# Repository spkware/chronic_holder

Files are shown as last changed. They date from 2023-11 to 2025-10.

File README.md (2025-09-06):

# ***indie*** - ***in***dependent ***d***ovetail ***i***mplants for ***e***lectrophysiology

**Please check out our [preprint](https://www.biorxiv.org/content/10.1101/2023.12.22.572441v2) for more details on the approach!** 

Design files and instructions for manufacturing NP1.0, NP2.0alpha, and NP2.0 Neuropixels chronic recording enclosures. 

**Please reach out to us if you want to try this approach, we need your input.** We are actively working on the instructions.

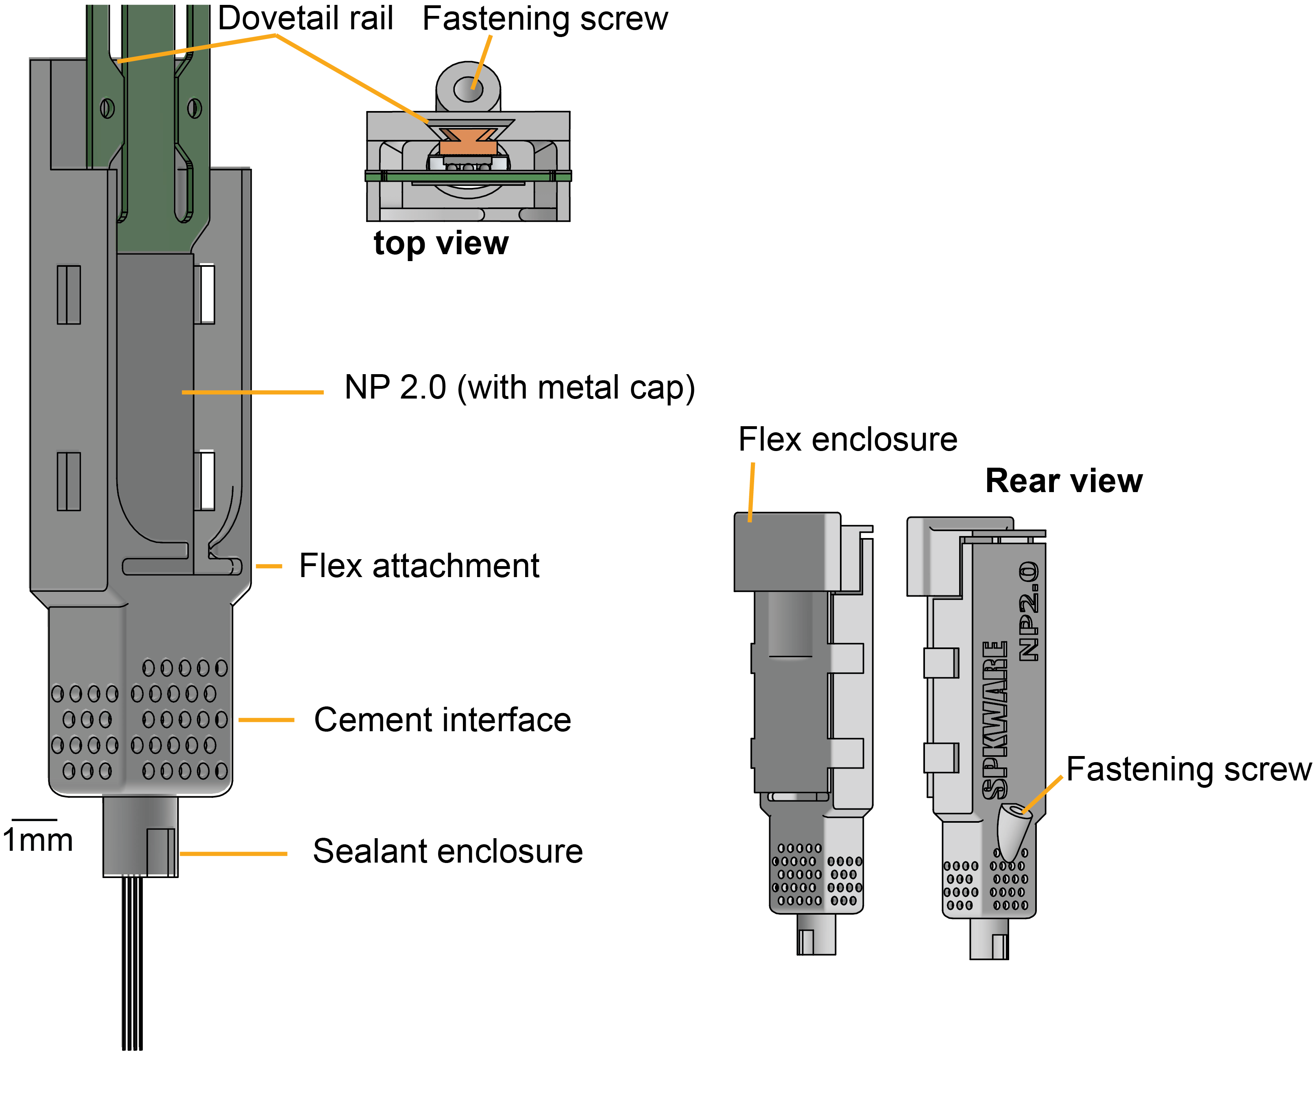
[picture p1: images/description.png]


These probe enclosures use the dovetail to secure the probes, the design is at the *current limit of the printing resolution of the SLA technology* and for that reason, it is sensitive to the material, and to the washing and curing steps. After printing, the screw hole has to be tapped using a standard 1mm thread tapper.

The NP1.0 holder weights 1.2g, the NP2.0 holder weights 0.57g. All weights include the respective probe, chassis and cap, but no headstage.

# Table of contents
- [Tools list](#tools-list)
- [Parts list (non-printed)](#parts-list-non-printed)
- [Assembly](#assembly)
  - [Printing holders](#printing-holders)
    - [General printing considerations](#general-printing-considerations)
    - [Recommended printer](#recommended-printer)
    - [Printing from STL](#printing-from-stl)
  - [Preparing the printed parts](#preparing-the-printed-parts)
  - [Preparing the probes](#preparing-the-probes)
  - [Mounting and recovering probes](#mounting-and-recovering-probes)
  - [Holder assembly for freely moving vs head-fixed experiments](#holder-assembly-for-freely-moving-vs-head-fixed-experiments)

# Tools list

The following lab tools and supplies are required:

| Name  |  Usage      |   Vendor     | 
|-------|--------------|-------------|
| Solder station | Solder wire to probes (if using external ground) | any |
| Fine tipped forceps | Handling probes | any ([example here](https://www.amazon.com/Scientific-Labwares-Precision-Stainless-Straight/dp/B07V3JF6JD/ref=sr_1_4?keywords=fine+tip+forceps&qid=1700025665&sr=8-4)) |
| Small phillips screwdriver (M1) | Secure probe in holder | any | 
| Tap wrench | Tap the plastic holder | any
| M1 tap | Tap the plastic holder | any
| Allen wrench | secure holder to stereotax | any| 
| Stoelting surgical stereotax | stereotaxic surgery | Stoelting (we will soon make stereotax arm attachments for other manufactures)
|Standard rodent surgical toolset | rodent surgery | any| 
| Narshige grinder (optional, but recommended) | probe sharpening | Narshige
|(Optional) Metal cap holder | Hold the probes for cleaning | [IMEC](https://www.neuropixels.org/) (There are different versions for the 1.0 and 2.0 probes, get the correct one for the probes you have)
|(Optional) Thorlabs breadboard, posts and rotating post clamps | Hold probes for washing. (It can be nice to use Thorlabs parts to build a dedicated washing setup to keep surgical rigs unoccupied, but you can also just use your stereotax) | Thorlabs

# Parts list (non-printed)
The following parts are required, not including the 3D printed parts.

| Name  |  Usage      |   Vendor     | 
|-------|--------------|-------------|
| Neuropixels probe (1.0/2.0alpha/2.0) **with metal cap** | record neural activity | [IMEC](https://www.neuropixels.org/) |
| Putty | Temporarily store assembled holders | any
| M1x4 (NP2) or M1x5 (NP1) phillips head screw | secure probe to holder | any
| Bolt (M2, allen key) | stereotax holder, 1x per stereotax arm you plan to use | [Amazon](https://www.amazon.com/Machine-Assorted-Stainless-Assortment-Threaded/dp/B0DFWWFY4Q/ref=sr_1_4?crid=2UCBD7LKSA5SO&dib=eyJ2IjoiMSJ9.eNHLdrJc9lPFJbB2M1D_otWzLYXCDLBKCyQ_V31EDA7siOJkOj9CHxbrd82vGMWiKzanTB4pLcinpIn6ZhEveg10mtvRLkSY-F-6g6sw5p1VZBKMb5nrkJdZkhmVTz5aFlPg6q9OBeEWQFuS0SnWiNbBMR6pGfe90Mv7BW3MsjYeQxkkVDCqbt99_g5Bc91IAjSIfIt5EnJVr-JwgREakpEo0WQ0wsOO980k-tfUlpE.FvCf3cdy6SweoLbAyzSe15mPmmei50MwVvm74pP6g8s&dib_tag=se&keywords=230+Pcs+m2+stainless+steel+screws+nuts+assortment+kit&qid=1733427815&sprefix=230+pcs+m2+stainless+steel+screws+nuts+assortment+kit%2Caps%2C107&sr=8-4)
| Nut (M2) | stereotax holder, 1x per stereotax arm you plan to use | [Amazon](https://www.amazon.com/Machine-Assorted-Stainless-Assortment-Threaded/dp/B0DFWWFY4Q/ref=sr_1_4?crid=2UCBD7LKSA5SO&dib=eyJ2IjoiMSJ9.eNHLdrJc9lPFJbB2M1D_otWzLYXCDLBKCyQ_V31EDA7siOJkOj9CHxbrd82vGMWiKzanTB4pLcinpIn6ZhEveg10mtvRLkSY-F-6g6sw5p1VZBKMb5nrkJdZkhmVTz5aFlPg6q9OBeEWQFuS0SnWiNbBMR6pGfe90Mv7BW3MsjYeQxkkVDCqbt99_g5Bc91IAjSIfIt5EnJVr-JwgREakpEo0WQ0wsOO980k-tfUlpE.FvCf3cdy6SweoLbAyzSe15mPmmei50MwVvm74pP6g8s&dib_tag=se&keywords=230+Pcs+m2+stainless+steel+screws+nuts+assortment+kit&qid=1733427815&sprefix=230+pcs+m2+stainless+steel+screws+nuts+assortment+kit%2Caps%2C107&sr=8-4)
| Fine grit sandpaper (>1000) | Sanding down support attachment points | any
| (Optional) Kapton tape | secure probe and silver wire for soldering | ULine
| Kwik Sil | cover probes and craniotomy during surgery | WPI
|Silver Epoxy|coat grounding wire and ground screw|MG Chemicals 8331D Silver Conductive Epoxy
|  **Bare** silver wire, 0.010 in diameter | grounding, if external grounding is desired | [AM Sytems (Cat. no 782500)](https://www.a-msystems.com/p-756-bare-silver-wire.aspx?srsltid=AfmBOoob5PKCLHF8Wfljej8tYA_QrxX0-WfACrYPfjjLwrkzZmBuAf_l)

# Assembly
There are 7 total steps to using this design for your experiments: 

1. Printing the parts
2. Preparing the holder
3. Prepare the probe(s) (sharpening, soldering)
4. Mounting the probe in the holder
5. Implantation surgery
6. Probe Explantation
7. Probe cleaning

## Printing holders

**You may have to adjust the tolerances depending on the printing and washing protocol you use**, we provide scripts - iLogic - to do this programatically from **Autodesk Inventor 2025** - unfortunately backwards compatibility is not supported. You can get an academic license for Inventor if you work in an academic institution at zero cost.

**Do not implant probes without testing the tolerances.** We tipically print an array of differenet tolerance values to find out the one that fits best, then use that tolerance for all holders. 

### Recommended printer

| name  |  usage      |   vendor     | cost estimate | 
|-------|--------------|-------------|---------------|
|  [Form 3+](https://formlabs.com/store/3d-printers/form-3-basic-package-without-service/#/package/)| SLA printer  | Formlabs | around 3k (2023) |
| Form Wash | wash parts | Formlabs | around 650 (2023) |
| Form Cure | cure parts | Formlabs | around 750 (2023) |
| [Resin tank]() | 3d printer tank (needs to be replaced from time to time) | Formlabs | around 150 (2023) |
| [Grey Pro resin](https://formlabs.com/store/materials/grey-pro-resin/) | resin to print the holders (needs to be replaced from time to time) | Formlabs | around 200 (2023) |
| [Isopropyl 99%](https://support.formlabs.com/s/article/Isopropyl-Alcohol-IPA) | wash parts | multiple vendors | 150 per gallon |

Read the printer instructions for tricks on how to print, wash and cure. Washing times depend on how clean the isopropyl is and strongly affect the tolerances.
### General printing considerations
We used a **FormLabs Form 3+ printer** and **GreyPro resin** to develop these protocols, please let us know if you use another printer or resin. *Clear*, and *Rigid 10k*, will NOT work (too brittle). Black V2 also worked in our hands but was not as good. Check [#2](https://github.com/spkware/chronic_holder/issues/2) for an alternative material using a commercial vendor ( thanks @wangxuanyu0419 ).

Each version NP1.0, NP2.0 and NP2.0alpha has a folder in the repository. Print using the files in the **stl_exports** folder and using **PreForm** . 

   -  the **main chassis** is printed standing **vertically** and with the **dovetail side facing the mixer**, we tested other orientations, this was the most reliable. Do not use internal supports nor supports in the dovetail rail. This part is very sensitive to the location of the supports and printing orientation.
   - we print the *cap* (with and without headstage)  and the *stereotax holder* parts at an angle with the outer part facing the bottom, no internal supports.

### Included preform files
Under the [Releases Page](https://github.com/spkware/chronic_holder/releases/) we have provided PreForm files with these support structures already defined. We **highly recommend** printing from these files if you can. Just adjust the numbers of each part as needed, but keep the support structures. However, if you need to adjust the designs and print your own, we provide instructions below.

### Printing from STL (creating your own PreForm files)

Tested on PreForm 3.32.0. **Layer tickness 0.050mm** with **GreyPro resin**.

1. Drag the STL file(s), acknowledge *ignore* if it prompts for "issues"
2. The holder chassis needs to be **vertical**. Orient the **dovetail to the mixer side**. On the **orientation** menu: Orient Y by 90 deg, orient Z by 180 (for NP2 and NP2a; NP1 will load already facing the mixer side)
3. On the **supports** menu: remove internal supports, density 0.8, touchpoint size 0.45mm.
4. Click *Auto-generate* supports, then **edit** and remove supports that are in the dovetail. Put the support that is in the entrance of the dovetail closer to the bottom/back side.  
5. Copy-paste after the supports are generated, as many copies as need.

Printing should take <7 h depending on how many parts are being printed. After printing, **wash for 15-20 min** depending on how clean is the isopropyl is, and let dry for at least 4 h (avoid sun light). If the parts feel "sticky" after this drying period, wash for 2 additional minutes. Cure the parts in Form **Cure with the default settings for Grey Pro**. 

## Preparing the printed parts

Once the plastic parts are printed, a few key steps need to be taken to prepare them for use.
1. First, carefully remove the plastic parts from their support structure using forceps and surgical scissors. Care must be taken to not break the small tabs that will hold the flex cable.
2. Sand the support attachment points down with a fine grit sandpaper (grit $\ge$ 1000). This only needs to be done for the main chassis part, but it is important to remove any surface irregularities from the support attachments that could affect how the chassis fits into the stereotax holder.
3. Tap the parts using a standard tap wrench with M1 tap. Be sure to apply a fair amount of forward pressure while tapping, otherwise you may strip the plastic. 
4. Blow out any plastic powder that made its way inside the chassis from the tapping process. 
5. **Test the dovetail mechanism**. Do this with a dummy or a broken probe and ensure that the probe slides along the dovetail socket before trying with a real probe.

### Stereotax arm setup
When setting up the stereotax holder attachment, remove the screw from the end of the Stoelting stereotax arm. Attach the base stereotax arm part (`stereotax_holder_part_1`) with this same screw. Then attach `stereotax_holder_part_2` to part 1 with an M2 nut/bolt. The M2 bolt is loosened and tightened in order to secure and release the chassis during implantation.

## Preparing the probes

1. Sharpen the probes, this reduces resistance when inserting and on mice is often sufficient to puncture the dura, meaning a durotomy is not needed. To sharpen, we use a Narshige grinder set to 70 and sharpen for 5 minutes. Be sure to sharpen the side that does not have the contacts. 

2. Soldering. We have found that it works best to solder the ground and reference together for each probe and then connect these all to one ground screw. The ground screw should not be next to any muscles to minimize artifacts. We have tried using internal reference (where no ground screw is used and instead the tip of the probe is ground) and recordings were lower quality. We recommend using a ground screw. After wrapping the silver wire around the ground screw, we cover it with silver epoxy to ensure solid conduction.

## Mounting and recovering probes

The design uses the "metal cap" (aka dovetail) to guide and secure the probe (through a screw in the rear of the holder). **To use this implant design, we recommend you order the probes denoted "with metal cap" on the IMEC website.** If you already have probes without the metal cap and want to use this design, you can have the metal dovetail machined yourself and then glue it to the probe. We will provide the design files for that part and instructions on how to glue it soon.

To mount probes, insert the probe with the shank first throught the dovetail, drive it all the way with the help of forceps.

**Critical:**
   - The probe should not be wiggling when it reaches the bottom of the holder. The fit should be snug (if the probe wiggles side to side when you move the flex, the dovetail tolerance is too large).
   - Secure the probe with an M1 screw. We will post pictures of how to tap the holder and secure the probe (this should be done before trying to mount the probe in the holder.)
   - Lift the flex, the probe metal cap should be flat in the rail (if the probe is not sitting flat in the dovetail, the tolerance is a bit too large.)

To "recover" do the oposite:
   - release the screw
   - use your thumb in the back of the holder
   - pull the probe by the flex, up the rail until the shank is entirely out,
   - either slide the cap out or rotate the probe down 45 degrees to break the rails.



## Holder assembly for freely moving vs head-fixed experiments

The indie can be used for both freely moving and head-fixed experiments. We have designed two different caps to facilitate this. 
- The head-fixed cap covers the main chassis and provides a slot to house the flex cable when not in use. Thus, the headstage must be connected to the flex cable for each recording session. 
- The freely-moving cap, has space to house the headstage on the animal. In this configuration, the headstage remains on the animal, even when in its home cage.

Both caps should be applied __after__ the surgery is complete. We recommend removing the animal from the stereotax and then putting the caps on. Instructions for assembling both caps are shown below.



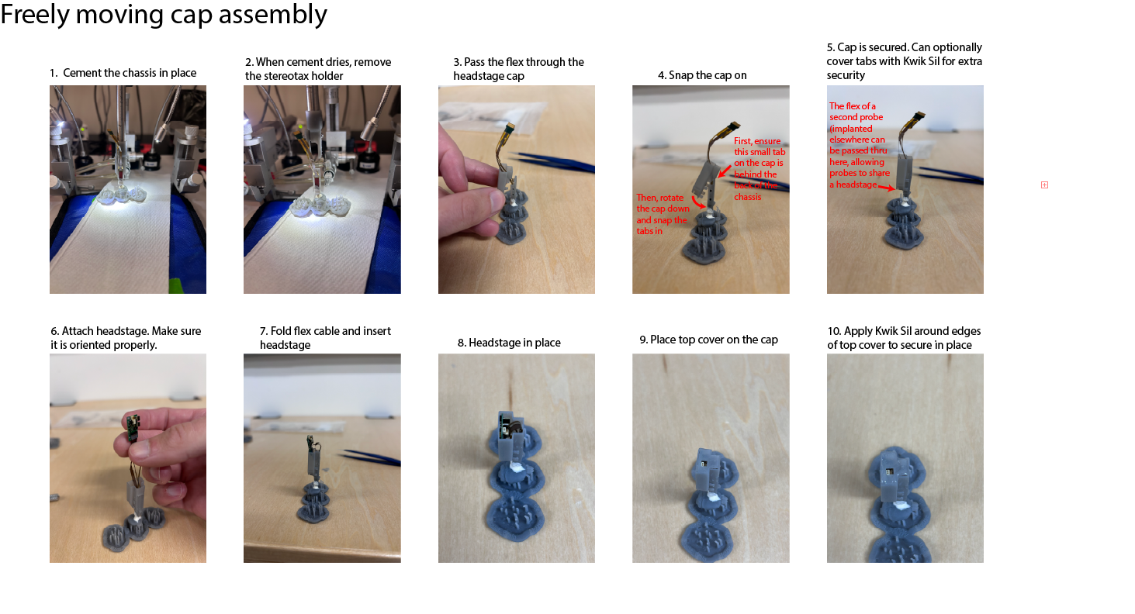
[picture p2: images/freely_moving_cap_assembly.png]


_____________________

These designs are not intended for commercial use or distribution.

Please reach out for feedback.
Max Melin (mmelin@ucla.edu) and Joao Couto (couto@ucla.edu)

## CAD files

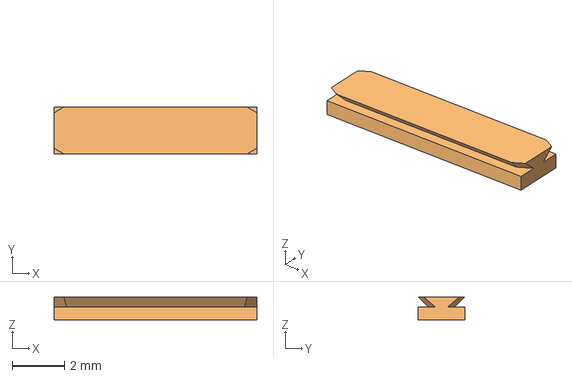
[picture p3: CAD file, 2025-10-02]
NP2/metal_cap/np2_dovetail.stp
7.80 x 1.80 x 0.88 mm

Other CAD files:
NP2/metal_cap/np2_dovetail_tech_drawing.dwg
NP1/1_main_chassis/np1_main_chassis.ipt
NP1/2_cap/cap_no_headstage/np1_cap_no_headstage.ipt
NP1/2_cap/cap_with_headstage/np1_cap_with_headstage.ipt
NP1/2_cap/cap_with_headstage/np1_headstage_cap_top_closure.ipt
NP1/3_stereotax_holder/np1_stereotax_holder_part1.ipt
NP1/3_stereotax_holder/np1_stereotax_holder_part2.ipt
NP1/np1_full_assembly.iam
NP2/1_main_chassis/np2_main_chassis.ipt
NP2/1_main_chassis/np2_main_chassis_no_through_holes.ipt
NP2/2_cap/cap_no_headstage/np2_cap_no_headstage.ipt
NP2/2_cap/cap_no_headstage/np2_cap_no_headstage_top.ipt
NP2/2_cap/cap_open_top/np2_cap_open_top.ipt
NP2/2_cap/cap_open_top/np2_headstage_box.ipt
NP2/2_cap/cap_open_top/np2_headstage_box_v2.ipt
NP2/2_cap/cap_with_headstage/np2_cap_with_headstage.ipt
NP2/2_cap/cap_with_headstage/top_enclosure.ipt
NP2/3_stereotax_holder/np2_stereotax_holder_part1.ipt
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

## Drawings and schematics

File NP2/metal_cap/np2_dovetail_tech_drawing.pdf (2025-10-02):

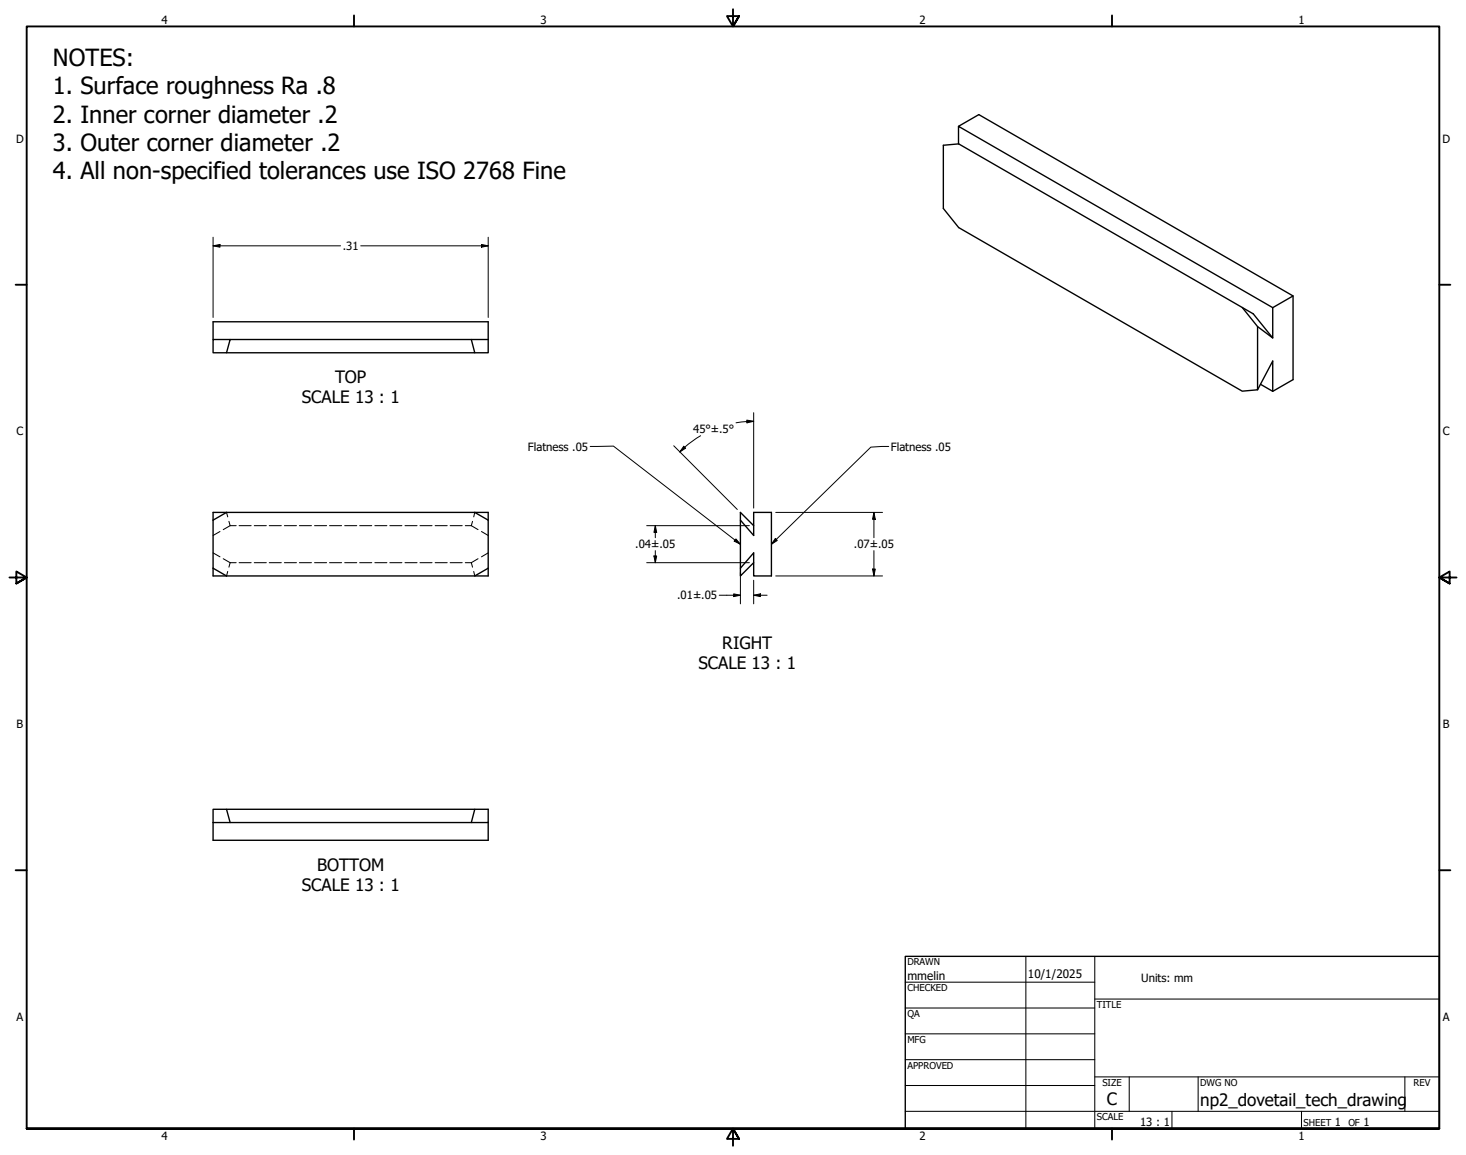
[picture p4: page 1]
SCALE 13 : 1; Flatness .05

NOTES:
1. Surface roughness Ra .8
2. Inner corner diameter .2
3. Outer corner diameter .2
4. All non-specified tolerances use ISO 2768 Fine

DRAWN mmelin | 10/1/2025 | Units: mm

CHECKED

MFG

APPROVED

SIZE C | DWG NO np2_dovetail_tech_drawing | REV

SCALE 13 : 1 | | SHEET 1 OF 1

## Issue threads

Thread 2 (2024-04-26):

### ISSUE TITLE
Guidance on cap assembly

### ISSUE THREAD

**Issue by wangxuanyu0419** [spkware/chronic_holder#2]
Hi Max and Joao!
I have printed your NPX2.0 holder from a local commercial 3D printing provider and it looks all fine. The probe can be fastened well (haven't tested in vivo yet). But for the cap, I'm not sure how it works. I need more guidance.
The cap with an open top (np2_cap_open_top) allows the flex cable to come out from the top, that works for me.
But the np2_cap_no_headstage_bridge, which you used in your preprint, it seems that the ZIF area can't go through the small opening from the inside. How did you assemble them? It would be good to add a few photos for the assembly of caps.

**Comment by jcouto** [comment]
Hi Xuanyu,
thanks for reaching out! Great that it worked from a commercial vendor, which one did you use in case others near you need fixtures?

The cap just slides into the fixture, does this image works? For head restrained recordings, I would use the cap that stores the flex.
![image](https://github.com/spkware/chronic_holder/assets/1855379/c6cb59fd-5b78-44a0-8ae0-f798e832bc20)

The cap that lets the flex come out the top is to be used when the headstage is also cemented. 

![image](https://github.com/spkware/chronic_holder/assets/1855379/70f3a494-6f0b-4151-bec9-086dfedaafe5)

We'll post a video of how to use the caps when we get a chance. Do these diagrams help for now?

**Comment by wangxuanyu0419** [comment]
Dear Joao:

Yes! The diagrams are very helpful! Thank you!

Regarding the vendor, I'm based in Munich, Germany, and the vendor is [Protolabs](www.protolabs.com/). I used ABS-Like Grey (_Accura Xtreme Gray_, SLA) which has comparable mechanical features as the GreyPro resin for your desktop printer. The minimum feature size was 0.254mm.
The main chassis was printed without any problem. The caps I received a warning from the vendor of thin walls, but it turned out to be alright. 

![img_20240415_140737_720](https://github.com/spkware/chronic_holder/assets/61549460/da02e29d-ddd7-4210-8342-c3f4c88f193e)

One following question regarding the first figure. Do you mean for prolonged implantation, it is recommended to apply KwikSil from outside to cover the junction between the cap and the chassis?

**Comment by jcouto** [comment]
We had caps that stayed for months without KwikSil, so it is not essential. 

In some cases the cap fell off (if the print was not ideal or the ground wire was on the way) in that case, we just put the cap back on and kept recording without issues. To prevent that if falls you can just add a bit of KwikSil which can be easily removed before extraction and keeps the implant clean.
 
That's great to know about the _Accura Xtreme Gray_, thanks for sharing!

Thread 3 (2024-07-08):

### ISSUE TITLE
Alternative design file format

### ISSUE THREAD

**Issue by JonathanAMichaels** [spkware/chronic_holder#3]
Could you provide the design files in any other format, for example STEP? Autodesk Inventor requires a Windows system.

**Comment by jcouto** [comment]
Hi @JonathanAMichaels, thanks for the message. 

We just published [release v1.0](https://github.com/spkware/chronic_holder/releases/tag/v1.0.0) with STL and STEP files. Please let me know if there are other formats that you find useful!

Our plan is to maintain the repo with our most recent design files (editable in Inventor) and issue releases with STL, STEP and PREFORM files that are "ready to print". 

PREFORM files can be used to print directly on FormLabs printers, STL and STEP to print from vendors or using other printers.

**Comment by JonathanAMichaels** [comment]
Thanks @jcouto this is fantastic!

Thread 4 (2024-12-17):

### ISSUE TITLE
Increase the wall thickness of the printed parts

### ISSUE THREAD

**Issue by YangLin916** [spkware/chronic_holder#4]
Hi Joao and Max!

Thank you so much for providing such great resources. Recently, I sent the 3D printing files to Xometry for printing, but they responded that some parts of the model are too thin. Their minimum printable thickness is 0.4 mm (0.015"). Could I trouble you to thicken the parts of these files with wall thicknesses less than 0.4 mm to meet this requirement? I’m not very familiar with design software, I’d greatly appreciate your help if possible!

The files are: np2_0.12, np2_0.112, np2_0.135, and np2_cap_with_headstage 

Yang

**Comment by jcouto** [comment]
Hi Yang, 

Thanks for reaching out. 

It is hard for us to change the size of the walls without re-sizing other parts and they print just fine on FormLabs with GreyPro resin and oriented vertically (instructions in the readme). We provide PreForm files in the releases. 

If you don't have access to a FormLabs printer, perhaps contacting the vendors or choosing another would be faster? We actually print in house but know of other groups that got successful prints from external vendors - check the readme please.

I hope it helps and it works by just changing vendors but feel free to reach out on mail if you want to chat about this. 

Best, Joao

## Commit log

2023-10-25 add 1.0 inventor files
    [NEUROPIXELS DOVE TAIL MOUNT.ipt, NP2_FLEX_00-01.ipt, np1_cap_no_headstage.ipt, np1_cap_with_headstage.ipt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]
2023-10-25 add 2alpha files
    [np2alpha_cap_no_headstage.ipt, np2alpha_cap_with_headstage.ipt, np2alpha_full_assembly.iam, np2alpha_headstage_cap_top_closure.ipt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]
2023-10-25 add np2production_version files
    [np2_cap_no_headstage.ipt, np2_full_assembly.iam, np2_main_chassis.ipt, np2_stereotax_holder_part1.ipt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]
2023-10-25 begin assembly instructions
2023-11-02 Folder structure remap.
    [np1_cap_no_headstage.ipt, np1_cap_with_headstage.ipt, np1_full_assembly.iam, np1_headstage_cap_top_closure.ipt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]
2023-11-02 iLogic saves the tolerance on the holder.
    [np1.ipt, np1_dovetail.ipt, np2_full_assembly.iam, np2_main_chassis.ipt]
2023-11-02 Re-linked NP1
    [np1_full_assembly.iam]
2023-11-02 Re-linked NP2alpha
    [np2alpha_full_assembly.iam]
2023-11-09 Added label to holder and stereotax parts. tolerances and update iLogic on NP1 and NP2.
    [np1_full_assembly.iam, np1_main_chassis.ipt, np1_stereotax_holder_part1.ipt, np2_full_assembly.iam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]
2023-11-09 Added STL exports for NP2
    [np2_0.125.stl, np2_0.13.stl, np2_0.135.stl, np2_cap_no_headstage.stl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]
2023-11-09 Added STL exports for NP1.
    [np1_0.127.stl, np1_0.13.stl, np1_0.137.stl, np1_0.14.stl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]
2023-11-10 add tab to freely moving cap to secure
    [np1_cap_with_headstage.ipt]
2023-11-11 table with printer
2023-11-11 Printer recomended headings.
2023-11-11 Details on printing
2023-11-11 Added mounting and recovering instructions
2023-11-15 Update assembly instructions
2023-11-20 Shorter room for kwiksil on np2.0.
    [np2_0.125.stl, np2_0.13.stl, np2_0.135.stl, np2_main_chassis.ipt]
2023-11-21 rework tabs
    [np2_cap_no_headstage.ipt]
2023-11-22 update tabs on cap with no headstage
    [np2_cap_no_headstage.ipt, np2_main_chassis.ipt]
2023-11-22 cap with open top
    [np2_cap_open_top.ipt]
2023-11-22 cap with headstage housing
    [np2_cap_with_headstage.ipt, np2_full_assembly.iam]
2023-11-22 headstage box prototype
    [np2_full_assembly.iam, np2_headstage_box.ipt]
2023-11-22 washing arm prototype
    [np2_full_assembly.iam, np2_headstage_box.ipt, np2_washing_arm.ipt]
2023-11-29 torus for washing
    [np2_washing_arm.ipt, wash_ring.ipt, washing_assembly.iam]
2023-11-30 np1 wash arm
    [np1_washing_arm.ipt, washing_assembly.iam]
2023-11-30 headstage box v2
    [np2_headstage_box_v2.ipt]
2023-11-30 washing stls
    [np1_washing_arm.stl, wash_ring.stl]
2023-11-30 update wash part tolerances
    [np1_washing_arm.ipt, np1_washing_arm.stl, np2_washing_arm.ipt, np2_washing_arm.stl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]
2023-12-01 add legs to headstage box
    [np2_full_assembly.iam, np2_headstage_box_v2.ipt]
2023-12-01 update np2 cap tabs
    [np2_cap_open_top.ipt, np2_cap_with_headstage.ipt, np2_full_assembly.iam]
2023-12-04 make washing setup rectangular
    [np1_washing_arm.ipt, np2_washing_arm.ipt, wash_ring.ipt, washing_assembly.iam]
2023-12-05 update stls
    [np1_washing_arm.stl, np2_full_assembly.iam, np2_washing_arm.stl, wash_ring.stl]
2023-12-08 update ilogic
    [np2alpha_cap_no_headstage.ipt, np2alpha_cap_no_headstage.stl, np2alpha_cap_with_headstage.stl, np2alpha_full_assembly.iam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]
2023-12-10 washing arm tolerances
    [np1_washing_arm.ipt, wash_ring.ipt, wash_ring.stl, washing_assembly.iam]
2023-12-10 update freely moving caps
    [np2_cap_with_headstage.ipt, np2_cap_with_headstage.stl, np2_full_assembly.iam, np2_headstage_box.ipt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]
2024-01-11 Added a mm extra room for the screw head.
    [np1_stereotax_holder_part1.ipt]
2024-01-25 ilogic for washing arm export
    [np2_washing_arm.ipt]
2024-02-17 smaller screw tolerance, move probe exit hole, smaller kwiksil tabs
    [np1_main_chassis.ipt]
2024-02-17 Stereotax holder changes for NP2. NP1 strenghtening on the taps. NP2 update.
    [np1_main_chassis.ipt, np2_0.125.stl, np2_0.13.stl, np2_main_chassis.ipt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]
2024-03-23 move probe exit hole
    [np1_main_chassis.ipt, np2_main_chassis.ipt]
2024-04-10 Removed stl files to replace with preform.
    [np1_0.127.stl, np1_0.13.stl, np1_0.137.stl, np1_0.14.stl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]
2024-04-10 Added preform file with grid and supports to find the tolerances and easy printing. Changed hole location, screw size and added text and ilogic for for NP2a.
    [np2alpha_main_chassis.ipt]
2024-06-06 update NP1 iLogic, small mods to freely moving cap
    [np1_cap_no_headstage.ipt, np1_cap_with_headstage.ipt, np1_headstage_cap_top_closure.ipt, np1_main_chassis.ipt]
2024-06-06 forgot assembly
    [np1_full_assembly.iam]
2024-06-06 update freely moving np2 cap
    [np2_cap_with_headstage.ipt, np2_full_assembly.iam, np2_main_chassis.ipt]
2024-06-06 update washing iLogic
    [np1_washing_arm.stl, np2_washing_arm.ipt, np2_washing_arm.stl, wash_ring.stl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]
2024-06-13 update screw size in readme
2024-07-01 Updated text to indie in prep for release 1
    [np1_main_chassis.ipt, np2_main_chassis.ipt]
2024-07-05 Updated part2 for stereotax (was old version due to binary missmatch). Added 130 and 135 tolerances to 2.0 indie
    [np2_full_assembly.iam, np2_main_chassis.ipt, np2_stereotax_holder_part1.ipt, np2_stereotax_holder_part2.ipt]
2024-07-23 Mention Inventor version in readme. Stereotax holder with deeper tabs.
    [np2_stereotax_holder_part1.ipt]
2025-03-12 Reduced tolerance on 2.0 stereotax holder.
    [np2_stereotax_holder_part1.ipt, np2_stereotax_holder_part2.ipt]
2025-03-13 Add opening for grounding wire to headstage cap
    [np2_cap_open_top.ipt, np2_cap_with_headstage.ipt, np2_full_assembly.iam]
2025-03-13 Add image of freely moving assembly instructions.
2025-03-20 Added a block to the np2 main, probe sits slightly higher in the holder. Added a slit to (in theory) prevent the flow of kwiksil up the shanks.
    [np2_main_chassis.ipt]
2025-06-01 NP2 main chassis with a longer block to seat the probe entirely on the dovetail. Better stereotax holder.
    [np2_cap_no_headstage.ipt, np2_main_chassis.ipt, np2_stereotax_holder_part2.ipt, np2alpha_main_chassis.ipt]
2025-10-02 dovetail part for machining
    [np2_dovetail.ipt, np2_dovetail.stp, np2_dovetail_tech_drawing.dwg]
2025-10-02 add cap stl
    [np2_dovetail.stl]
2025-10-06 Added alpha cap to let the headstage come out the top.
    [np2alpha_cap_flex_top.ipt]
